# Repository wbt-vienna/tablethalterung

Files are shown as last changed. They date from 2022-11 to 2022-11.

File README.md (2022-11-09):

# Flexible Tablethalterung

Diese Projektidee ist im Rahmen des [Hackathons für Assistierende Technologien](https://wbt.wien/hackathon) (April 2022) enstanden. Das Projekt "Flexible Tablethalterung" hatte zum Ziel, eine Tablethalterung für verschiedene Tabletgrößen zu erstellen, die dann auch auf einem 
Krankenhausbett oder Rollstuhl gut fixiert werden kann und verstellbar 
sein soll. Was bis zu diesem Zeitpunkt auf dem Markt zu finden war, war für Anwender und Anwenderinnen entweder zu teuer, nicht stabil genug oder passte von der Größe her nicht. Besonders für das für UK oft verwendete iPad Pro mit 12,9 Zoll Bildschirmdiagonale ist es schwierig passende, stabile Halterungen zu finden.

Für die Befestigung wurden Manfrotto Gelenksarme gewählt. Die Halterung besteht aus selbsterstellten 3D gedruckten Teilen und einem Metallprofil aus dem Baumarkt. Untenstehend finden Sie eine genaue Beschreibung, um sie selbst nachbauen zu können!

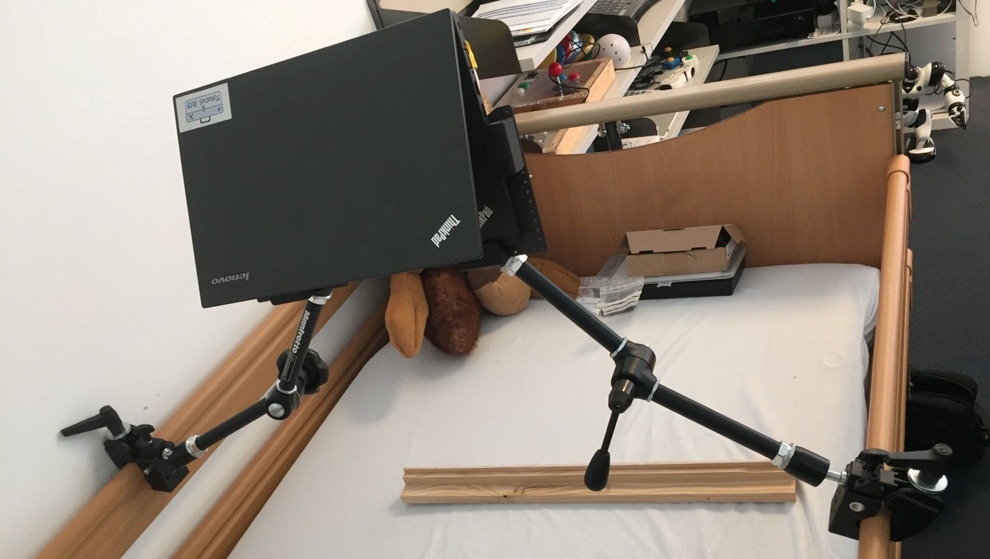
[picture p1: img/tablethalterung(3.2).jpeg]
tablethalterung


*Abb. 1: Tablethalterung*

## Materialliste

Folgendes Material wird für den Zusammenbau dieser Tablethalterung benötigt (in Abb. 2 und 3 entsprechend der Nummerierung beschriftet dargestellt)

1. 8 Stück Beilagscheiben

2. 4 Stück Senkkopfschrauben M4x12mm

3. 4 Stück Sechskantmuttern M4

4. 8 Stück Senkkopfschrauben M3x20mm

5. 2 Stück 1/4 Zoll - 20 x 3/4 Zoll UNC Sechskantschrauben, siehe [zollshop.de](https://www.zollshop.de/de/Zollschrauben-UNC-Stahl/Sechskantschrauben-UNC-Grade-5-8.8/14-Zoll-UNC/192/1/4-Zoll-20-x-3/4-Zoll-Laenge-19-05-mm-Sechskantschraube-UNC/)

6. 1 oder 2 Stück [Manfrotto Gelenksarme](https://www.manfrotto.com/global/photo-variable-friction-arm-italian-craftsmanship-244n/) 

7. Einen [Super Clamp](https://www.manfrotto.com/global/universal-super-clamp-with-ratchet-handle-035c/) pro Gelenksarm (1 oder 2 Stück abhängig von (6) ) zum Befestigen am Bett/Rollstuhl

8. 1 Stück Winkelprofil, beispielsweise aus [Stahl von Hornbach](https://www.hornbach.at/shop/Winkelprofil-Stahl-27x27x1-5-mm-1-m/8829116/artikel.html), in der Länge des Tablets / Computers

3D Druck:

9. 1 Stück [3D gedruckte Halterung linke Seite](./halterung_3dDruck-back_left_v2.stl)

10. 1 Stück [3D gedruckte Halterung rechte Seite](./halterung_3dDruck-back_right_v2.stl)

11. 4 Stück [Seitenteile](./seitenteile_v2.stl)

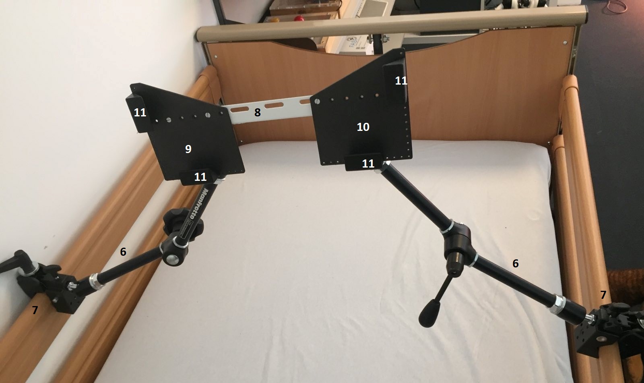
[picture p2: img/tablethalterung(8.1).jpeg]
material


*Abb. 2: Material*

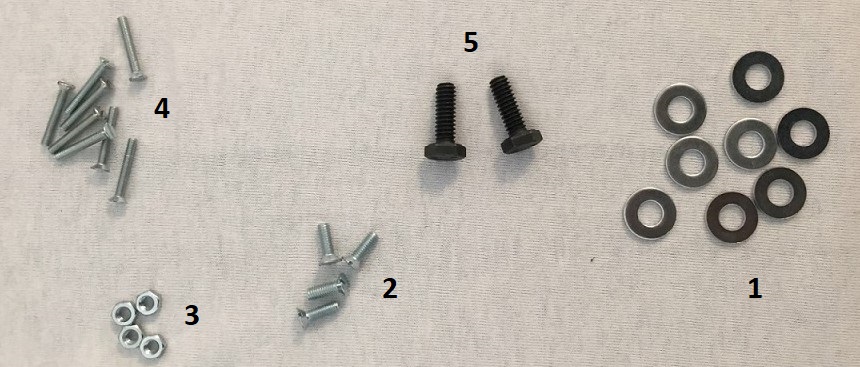
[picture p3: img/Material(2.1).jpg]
kleinmaterial


*Abb. 3: Kleinmaterial*

## Bauanleitung

1. Drucken Sie mit Hilfe eines 3D Druckers 1 Stück der [linken Halterung (9)](./halterung_3dDruck-back_left_v2.stl), 1 Stück der [rechten Halterung (10)](./halterung_3dDruck-back_right_v2.stl) und 4 Stück von den [Seitenteilen (11)](./seitenteile_v2.stl) aus anhand der verlinkten .stl Files. Falls Sie an der vorhandenen Zeichnung etwas adaptieren wollen, ist [hier](./halterung_3dDruck_v2.FCStd) der Link zur .FCStd-Datei (Klicken Sie zuerst auf den Link und dann auf "View raw").

2. Befestigen Sie 2 Stück der Seitenteile auf der linken Halterung und 2 Stück der Seitenteile auf der rechten Halterung mit Hilfe der Senkkopfschrauben M3x20mm (4). Pro Seitenteil brauchen Sie zwei Schrauben.

3. Schneiden Sie das Winkelprofil (8) auf die gewünschte Länge zu - am besten die gleiche Länge, die die längere Seite Ihres Tablets / Computers hat.

4. Befestigen Sie das Winkelprofil (8) auf der Rückseite der linken und der rechten Halterung. Verwenden Sie dazu pro Halterung 2 Stück Senkkopfschrauben M4x12mm (2) mit jeweils einer Sechskantmutter M4 (3) und 2 Beilagscheiben (1), siehe Abb. 4. Achten Sie beim Zusammenbau darauf, dass es an die Größe Ihres Tablets / Computers angepasst ist.
   
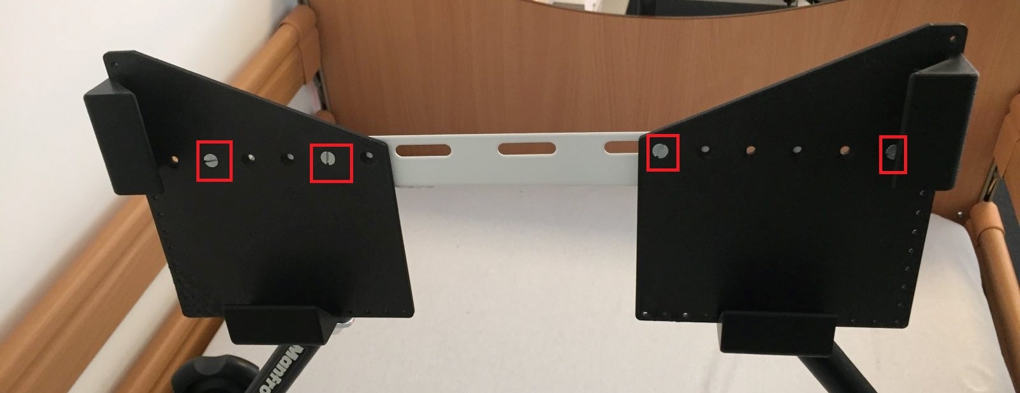
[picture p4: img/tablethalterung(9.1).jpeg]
halterungen
   
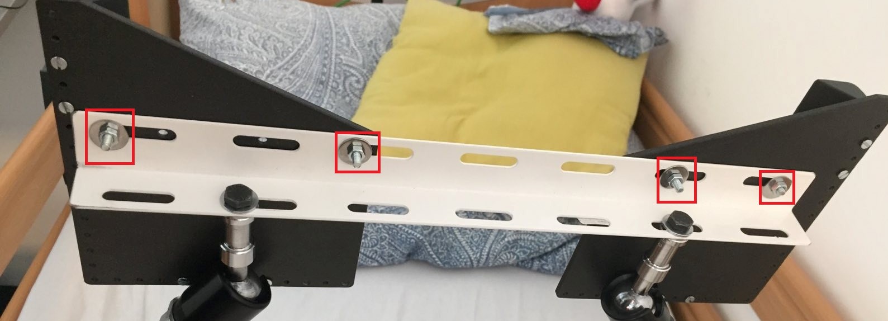
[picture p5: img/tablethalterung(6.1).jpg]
halterungen1
   
   
   *Abb. 4: Befestigung des Winkelprofils an den Seitenteilen*

5. Nun brauchen Sie den Manfrotto Gelenksarm (6) und den Super Clamp (7), um die Halterung am Rollstuhl oder am Bett (oder wo es für Sie notwendig ist) zu befestigen. Verwenden Sie pro Manfrotto Gelenksarm (6) jeweils eine 1/4 Zoll - 20 x 3/4 Zoll UNC Sechskantschraube (5) und eine Beilagscheibe (1), um den Gelenksarm am Winkelprofil zu befestigen, siehe Abb. 5.
   
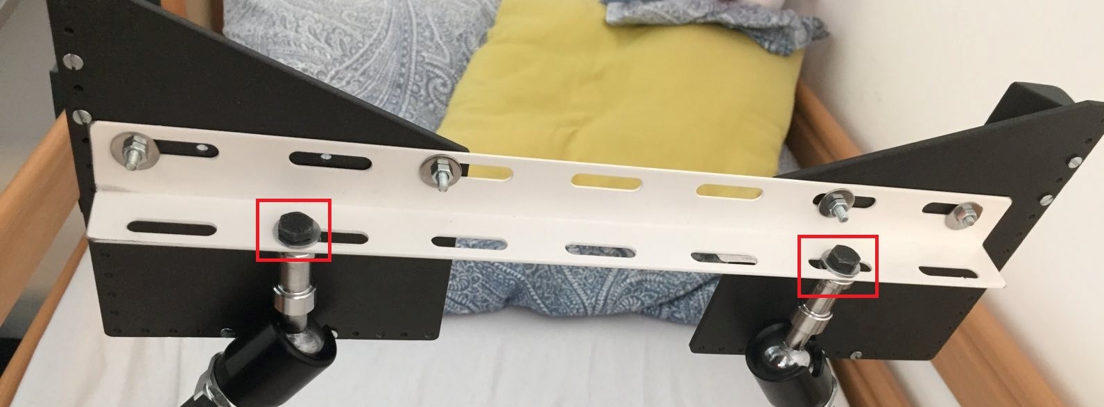
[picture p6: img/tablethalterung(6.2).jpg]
halterungen2
   
   
   *Abb. 5: Befestigung des Manfrotto Gelenksarm am Winkelprofil*

6. Befestigen Sie den Super Clamp (7) auf der anderen Seite des Manfrotto Gelenkarms (6), damit die Halterung am Bett / Rollstuhl oder ähnlichem befestigt werden kann, siehe Abb. 6.  
   
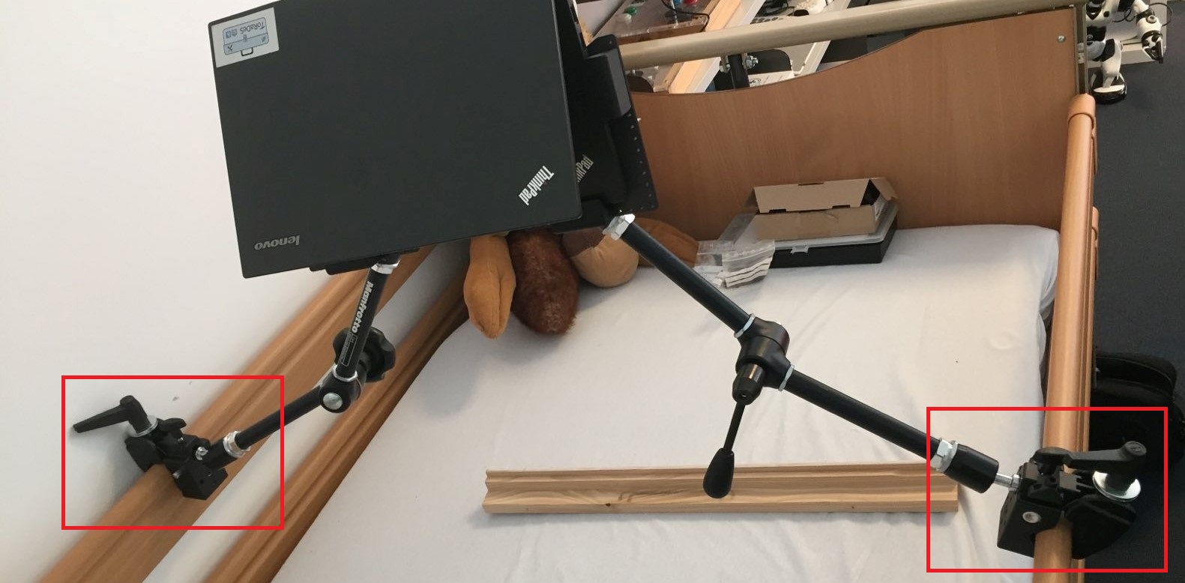
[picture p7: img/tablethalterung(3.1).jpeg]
   
   
   *Abb. 6: Befestigung des Super Clamps am Manfrotto Gelenkarm*

7. Auf unseren Abbildungen wurden zwei Manfrotto Gelenksarme (6) und daher auch zwei Super Clamps (7) verwendet, was die Stabilität um einiges erhöht. Alternativ kann auch ein Manfrotto Gelenksarm und ein Super Clamp verwendet werden. Hier würde der Manfrotto Gelenksarm mittig am Winkelprofil befestigt werden.

8. Nun können Sie die Halterung an der gewünschten Stelle montieren und Ihr Tablet / Computer in die Halterung hineinschieben. Viel Freude!

Zum Abschluss hier noch beispielhaft auf einem Rollstuhl befestigt:
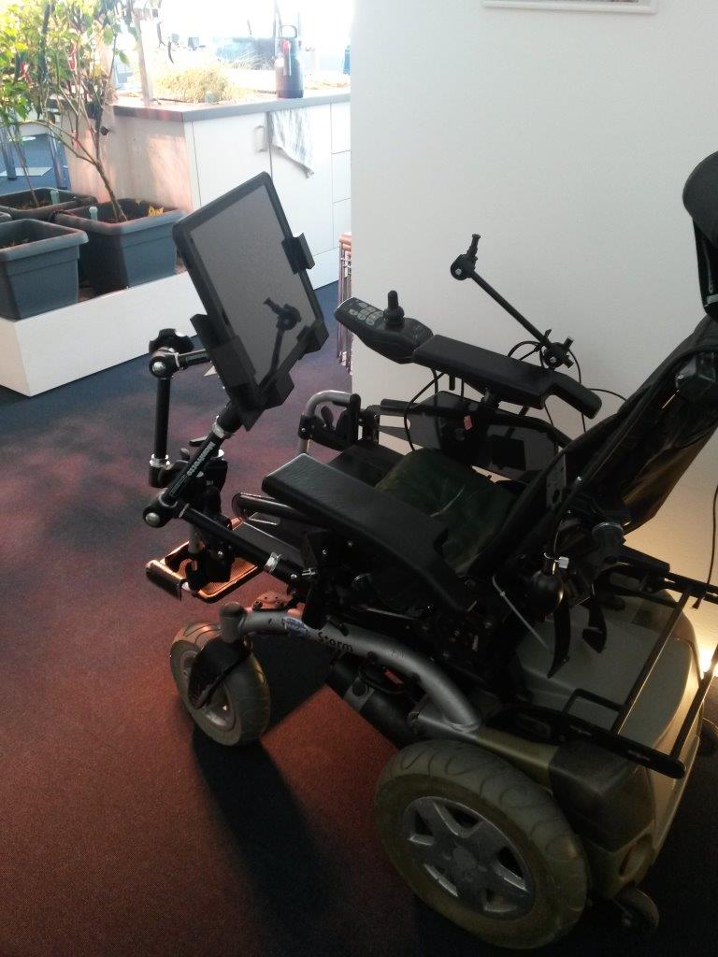
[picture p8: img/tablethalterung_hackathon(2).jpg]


   *Abb. 7: Befestigung der Tablethalterung auf einem Rollstuhl*

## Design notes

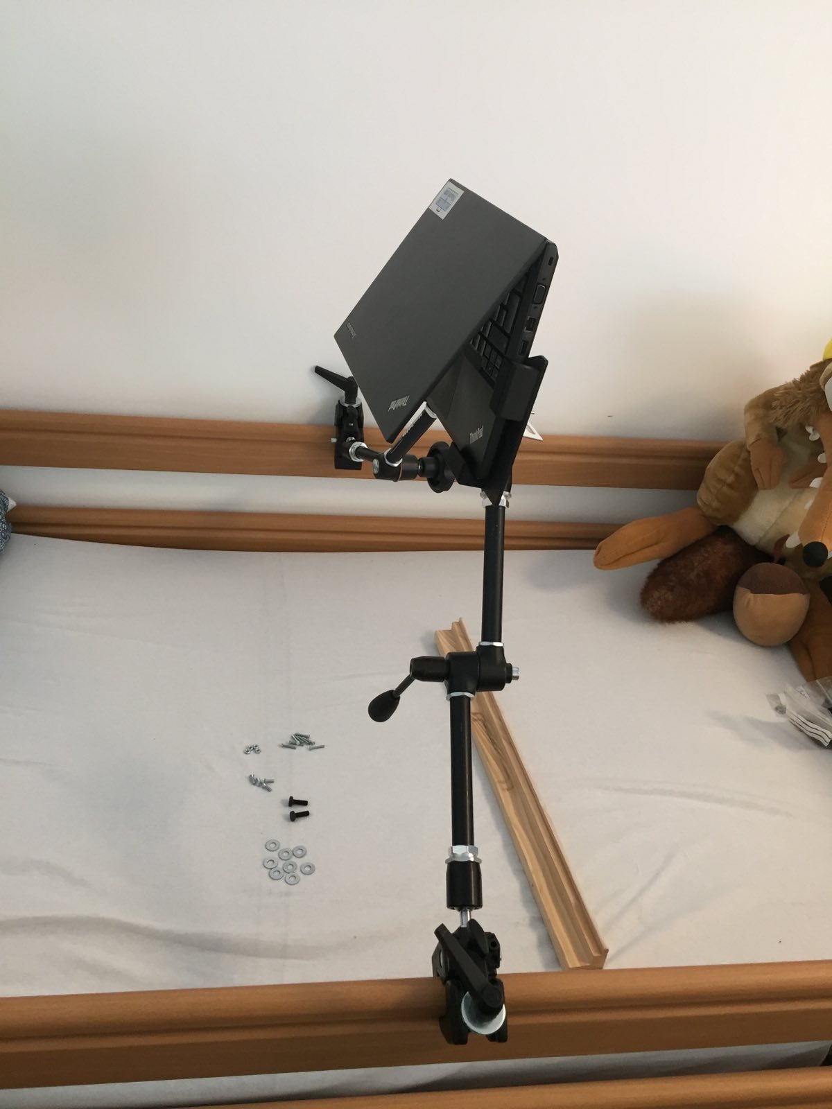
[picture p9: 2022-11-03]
img/tablethalterung(2).jpeg

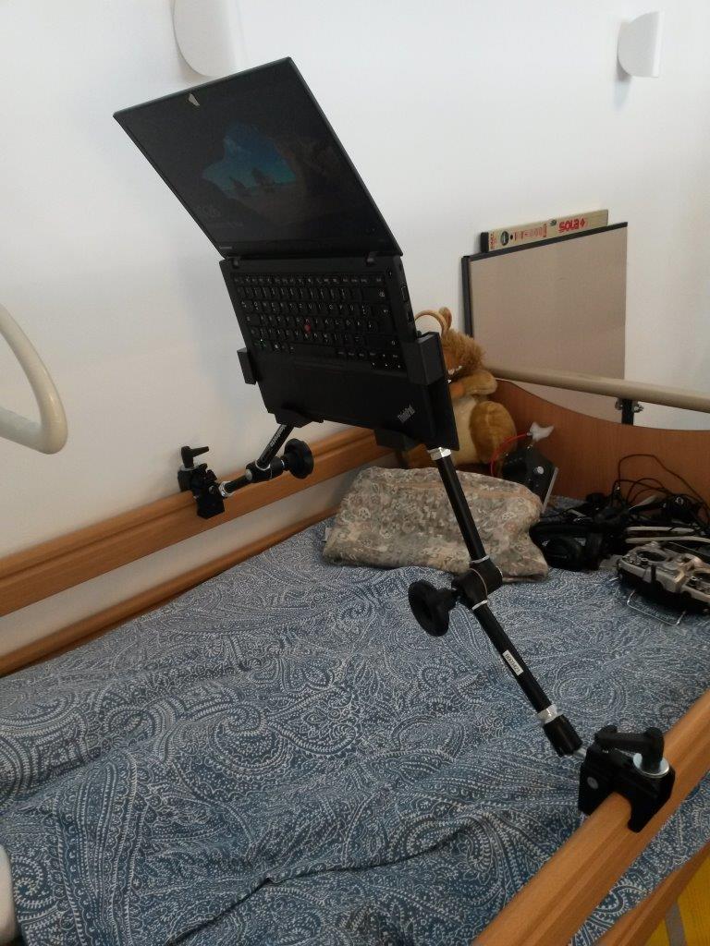
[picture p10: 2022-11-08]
img/tablethalterung_hackathon(6).jpg

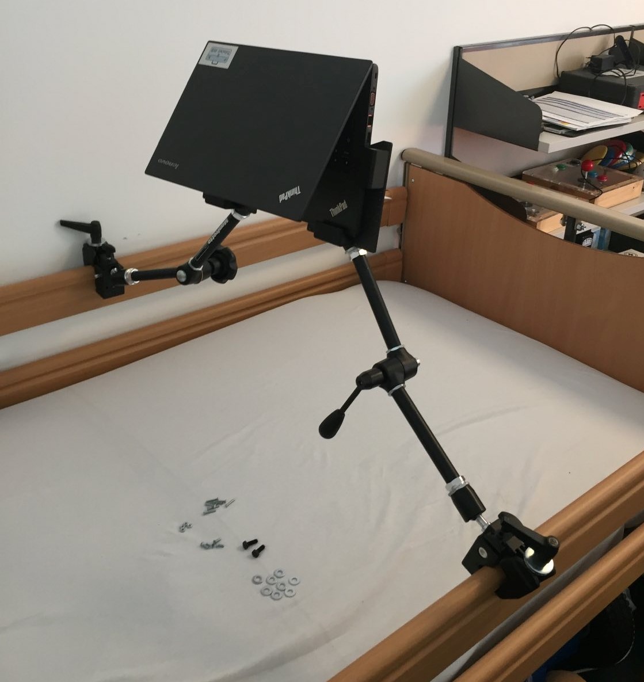
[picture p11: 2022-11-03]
img/tablethalterung(11).jpeg

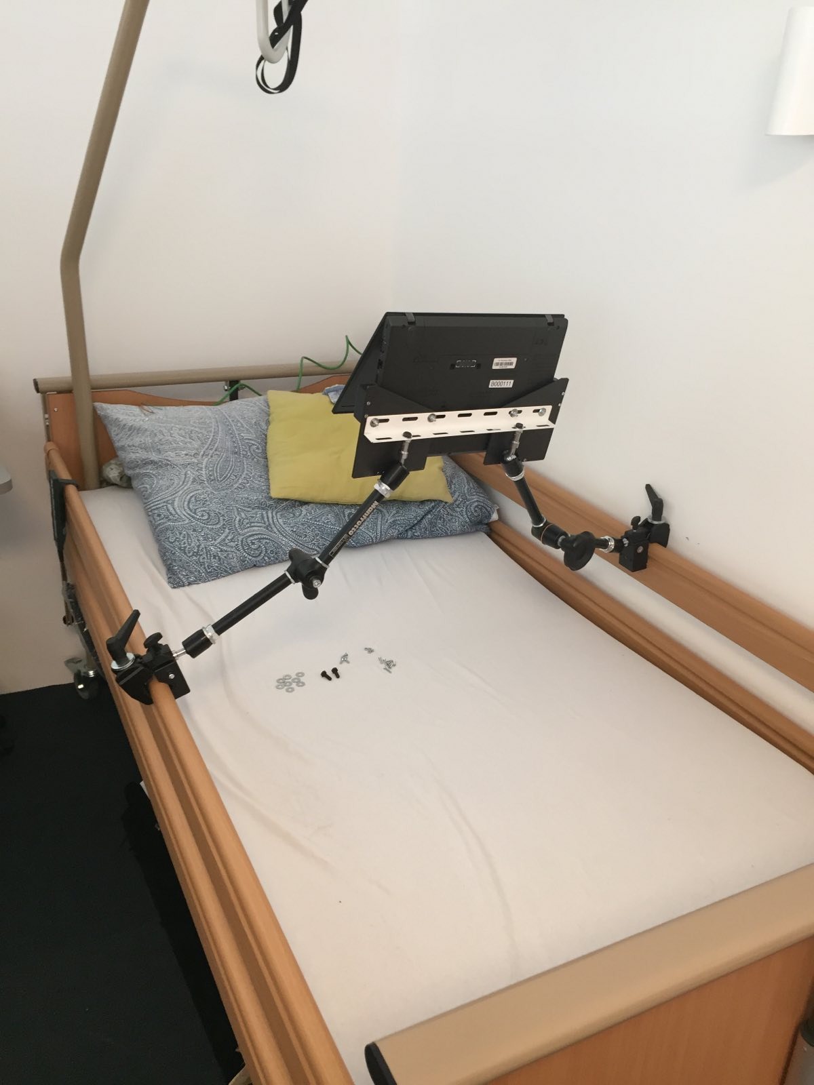
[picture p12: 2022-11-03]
img/tablethalterung(10).jpeg

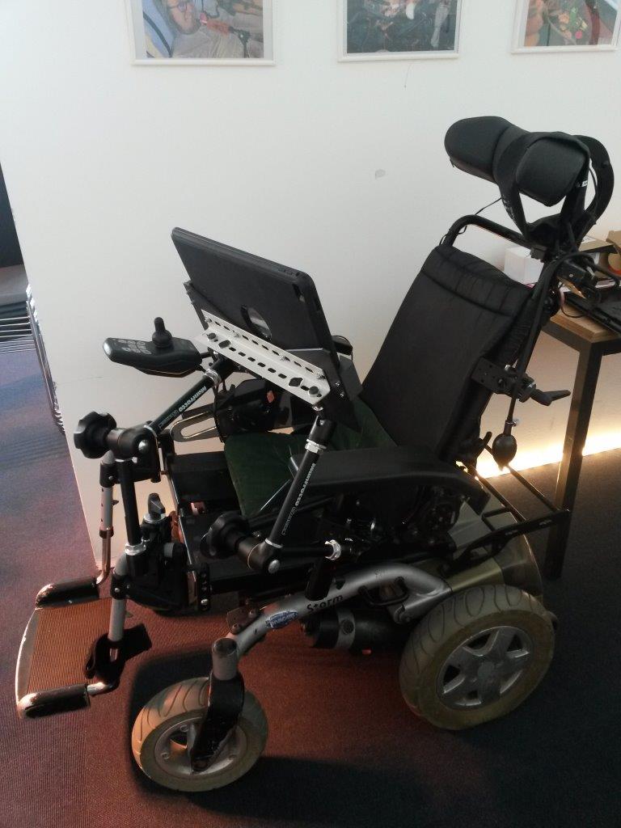
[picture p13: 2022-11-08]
img/tablethalterung_hackathon(1).jpg

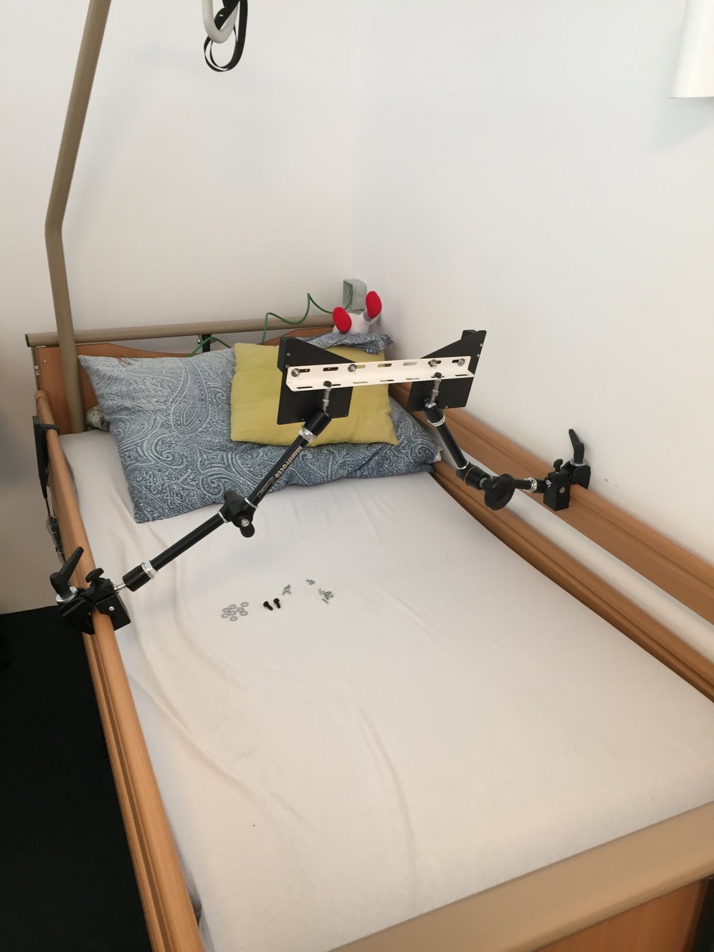
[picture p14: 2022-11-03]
img/tablethalterung(1).jpeg

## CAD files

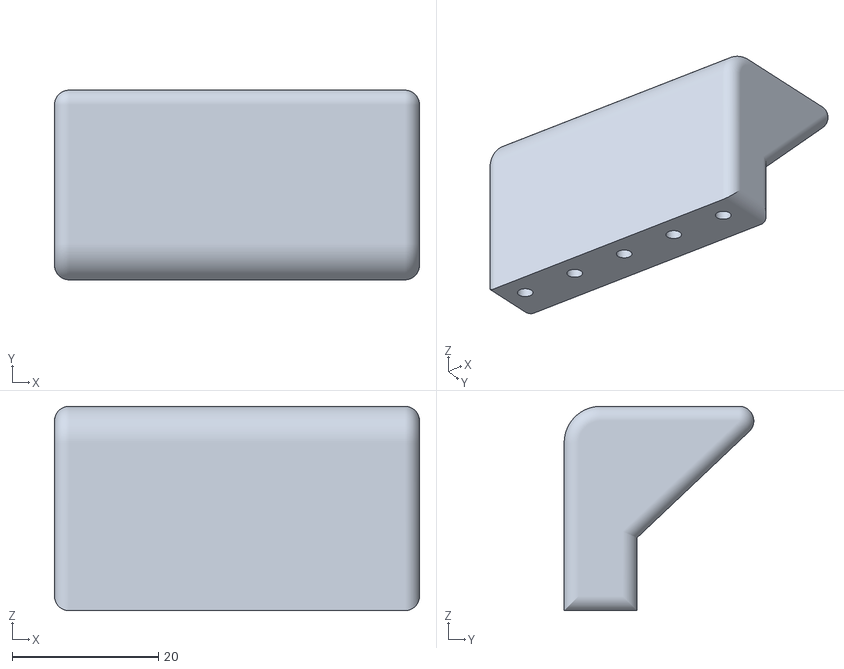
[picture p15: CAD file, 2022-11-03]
seitenteile_v2.stl
50.0 x 26.0 x 28.0

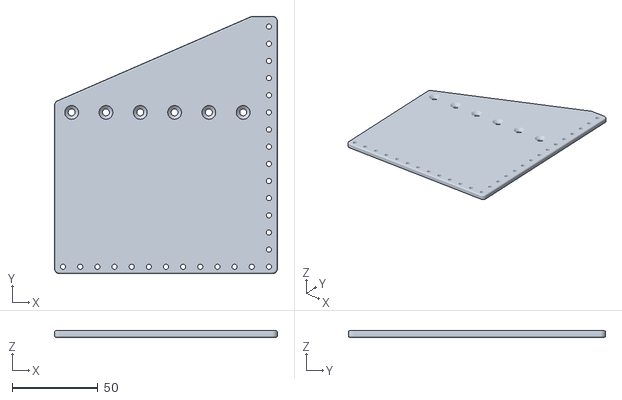
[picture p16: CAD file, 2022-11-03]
halterung_3dDruck-back_right_v2.stl
130.0 x 150.0 x 4.00

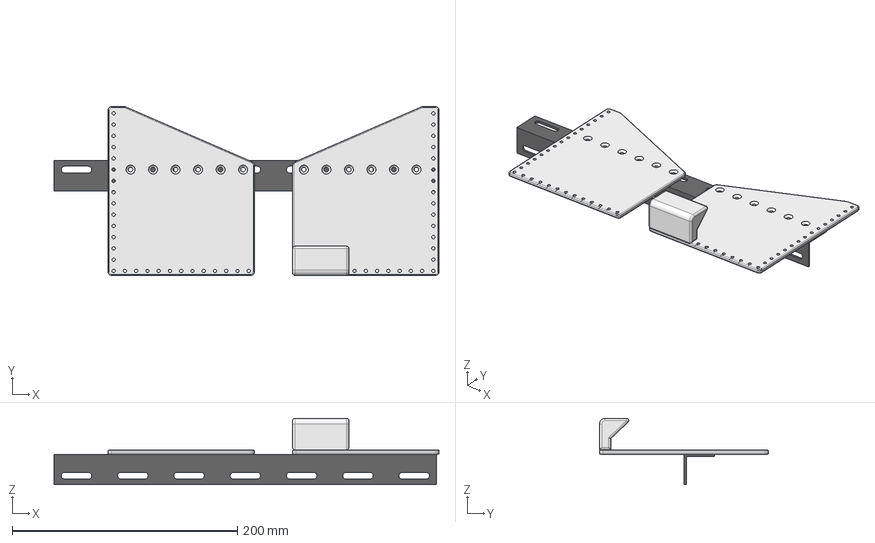
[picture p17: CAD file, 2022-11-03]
halterung_3dDruck_v2.FCStd
342.0 x 150.0 x 59.0 mm
back_right
back_left
montageecke

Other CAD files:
halterung_3dDruck-back_left_v2.stl
